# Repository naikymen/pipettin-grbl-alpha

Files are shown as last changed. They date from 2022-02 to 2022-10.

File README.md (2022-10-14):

# Development has moved to GitLab

New repoo at: https://gitlab.com/pipettin-bot/pipettin-grbl

# Pipettin' GRBL

Pipetting robotware for laboratory protocol automation.

> Proper documentation to build this yourself is not yet ready, let us know if you wish to get help, or help out :)

This repository contains hardware design files and software for a test prototype. 
Hardware is licenced under the [CERN-OHL-S](https://github.com/naikymen/pipettin-grbl-alpha/blob/master/HARDWARE_LICENCE.txt) licence 
and software under the [GNU GPLv3 licence](https://github.com/naikymen/pipettin-grbl-alpha/blob/master/SOFTWARE_LICENCE.txt) licence.

mender1_cdnm_mazinger

> Pardon our _castellano_ :)

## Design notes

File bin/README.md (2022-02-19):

# mongodb 3.2.12 binaries

Mongo compiled for 32-bit Raspbian in the Raspberry Pi 4. Unfortunately, the apt version did not work out for us.

See notes at `gui/README.md`.

## Startup commands

    sudo mongod --storageEngine=mmapv1

### Repair unclean shutdown

    sudo mongod --storageEngine=mmapv1 --repair
    sudo mongod --storageEngine=mmapv1

## CLI shell

    mongod

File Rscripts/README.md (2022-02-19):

# R code for pipettin-grbl

The PCR Mix protocol planner uses a custom R script, which clusters tubes by similarity into a dendrogram.
The resulting tree is cut, and intermediate solutions are prepared, reducing the amount of required pipetting steps,
and a consequently faster protocol. 

We use this version of R:

```
> R.version
               _
platform       arm-unknown-linux-gnueabihf
arch           arm
os             linux-gnueabihf
system         arm, linux-gnueabihf
status
major          3
minor          5.2
year           2018
month          12
day            20
svn rev        75870
language       R
version.string R version 3.5.2 (2018-12-20)
nickname       Eggshell Igloo
```

> R 3.5 is quite old, but this is what is packaged in `r-base` by our Ubuntu distribution for the raspberry pi.

## PCRmix protocol planner

### Requirements

* R 3.5.2
* Some packages: `install.packages(c("dendextend", "tidyr", "dplyr", "jsonlite"))`

### Code and usage

```sh
# First argument is the input JSON, and the second is the output JSON path
Rscript --vanilla ~/pipettin-grbl/Rscripts/pcr_planner.R ~/pipettin-grbl/Rscripts/sample_input.json ~/pipettin-grbl/Rscripts/sample_output2.json
```

See `pcr_planner.R`.

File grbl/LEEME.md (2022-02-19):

# Pipetting GRBL firmware

Vanilla GRBL 1.1h should work fine unless you need to control a servo (which you do need to use the tip ejector).

## Usage

Import this directory as a library in the Arduino IDE. Use the "grbl upload" example to burn GRBL onto the Arduino UNO.

If you have already installed the 10uF capacitor across the reset/abort pins (to prevent reset on serial reconnect), you may need to remove it temporarily before uploading the frimware (or you may get some errors while doing so).

## Testing

You may interact with GRBL from a linux terminal using `minicom`. For example:

```bash
minicom -D /dev/ttyACM0 -b 115200
```

Try typing `?` to check GRBL's status, or `$$` and pressing enter to see its settings.

The python scripts offer a rudimentary interactive text-based interface, using the `--interactive` option. That one wraps the serial interface, and controls other parts of the machine (i.e. the tool/pipette axis).

## Modifications

All major modifications are on the hardware side, specially on the Arduino CNC Shield 3.0 clone.

*IMPORTANT*: `ENABLE_DUAL_AXIS` and `VARIABLE_SPINDLE` are incompatible in our setup (though in theory its not impossible to enable them simultaneously).

### Servo control via Variable Spnidle PWM

If using a servo motor on the spindle enable pin, enable variable spindle with `#define VARIABLE_SPINDLE` (at line 339 of `config.h`).

The spindle PWM frequency is altered in `cpu_map.h` to be compatible with a hobby servo. Using a 1024 prescaler in fast-mode PWM we get `~60 Hz` which worsk great for ejecting tips.

Note: we tried to use this for the pipette axis. But the servo was not precise enough, and had a "bounce" effect which cannot happen during pipetting.

Ver wiki:

  * https://wiki.frubox.org/proyectos/diy/cnc#controlar-un-servo-con-el-spindle

### Dual Y axis Gantry squaring

This is disabled in our build. Our A axis clones the Y axis.

If you have dual X or Y axis (ie, two independent steppers and threaded rods for one direction of movement) enable gantry squaring with `ENABLE_DUAL_AXIS`. Follow the official GBRL documentation for correct configuration and limit switch setup.

## Configuration notes

I advise not using `$1=255` as it does not seem to play nice with our testing hardware (with A4988 drivers).

The full configuration for our setup makes GRBL work in positive space coordinates with origin at X0 Y0 by setting the masks correctly and issuing the corresponding G92 command after homing.

We also needed to reverse the Y axis and the XT homing direction. This is because the web-based GUI uses that coordinate system (right and down are positive the directions) and because reversing the homing direction will leave the machine at this origin (it otherwise homes to max X/Y instead of min X/Y).

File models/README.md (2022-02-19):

TODO: reorganizar este readme.

TODO: agregar info de modelos pasados a FreeCAD bajo `modelos_ejez_Z_y_S/basic_parts_freecad/`.

# Sujetador Jeringas y Pipetas

Sujetador Jeringa CNC Stepper.stl en modelos_ejez_Z_y_S/

Diseño en TinkerCAD para el "eje pipeteador" que usa:

  * Una jeringa
  * Stepper NEMA 17
  * Varillas de 8 mm
  * Varilla roscada de 8 mm con tuerca.
  * Tuercas y tornillos M3 / varilla roscada y tuercas de 3 mm

Link: https://www.tinkercad.com/things/gWPShCd3e0L-sizzling-lappi-borwo/edit

## Requires

  * `topeJeringa1mL` en modelos_pipetas_jeringas/

# topeJeringa1mL

Diseño en FreeCAD para la "T" en la parte de arriba del émbolo de una jeringa de 1 mL.

Marca "Bremen", marcada como: "Tuberculina 1mL con aguja 0.5 x 15 mm 25Gx5/8".

# Otro modelo

https://www.thingiverse.com/thing:1684481

https://www.tinkercad.com/things/aL2rLg0KME9

# Meshroom folders

Photogrammetry test, to digitize pipettes.

https://www.youtube.com/watch?v=1D0EhSi-vvc

https://meshroom-manual.readthedocs.io/en/latest/tutorials/sketchfab/sketchfab.html

# Notas

## Pipette tip dimensions

https://www.fts.co.nz/image/data/PDF/Pipette%20Tips.pdf

  * p1000 ~ 70 mm
  * p200 ~ 50 mm
  * p20 ~ 37-46 mm

Por lo tanto el eje Z debería poder viajar al menos 70 mm.

El eje Z del CNC solamente tiene 30 mm de viaje aproximadamente.

En un caso razonable, en el que haya un falcon de 50 en el workspace para usar con una p1000, el recorrido mínimo para poder pipetear todo debería ser 140 mm.

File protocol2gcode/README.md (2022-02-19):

# protocol2gcode

This python3 module works as three things:

* Interpreter: loads "protocol" actions and "platform" and "workspace" objects from MongoDB, defined previously through the GUI.
* Slicer: parses "actions" and generates "GCODE" for the protocol.
* Driver: controls GRBL, the pipette motor and the tip-eject servo motor. Sends commands to the machine (either from a predefined task/protocol in the mongo database or from a basic "interactive" interpreter).

## Commands: GCODE and Pseudogcode

### GCODE

"Vanilla" GCODE passed on to GRBL to move the XYZ axis.

The spindle `M3` command is used to eject tips (see electronics readme):

  * Eject: `M3 S20`
  * Retract: `M3 S150`

### Pseudogcode

Defined at `driverGcodeSender2.py`.

Used by the intepreter to move the pipette "P" axis:

  * `Phome;2` home the pipette and retract 2 mm away from the limit switch.
  * `Pmove;5` displace the pipette 5 mm
  * `Pmove;-5` displace the pipette -5 mm

It also supports a "wait" command:

  * `Wait;2` waits 2 seconds before parsing next line in the protocol.

The prefixes used (stuff beforethe semicolon) can be overriden.

## Dependencies

`sudo apt install python3-pip`

`pip3 install pyserial pigpio rpi.gpio`

`pip3 install pymongo==3.4.0`

La versión 3.10 no se lleva bien con mongodb disponible en los repositorios de Raspbian.

`sudo apt install pigpio`

`pip3 install python-socketio`

Note: installing bare 'socketio' may not work (https://github.com/miguelgrinberg/python-socketio/issues/264#issuecomment-518011401).

Note: if you find errors using "pip" to install the package in arch, try `sudo pacman -S python-socketio`

### pigpio and 64-bit OSes

There are some kernel problems. They were suposedly fixed in V71 or even before that, but i couldnt get it to work in Ubuntu Server 20.04 for RPi 4. The proposed solution involved:

  sudo nano /boot/firmware/cmdline.txt

Adding at the end of the line: `iomem=relaxed strict-devmem=0`

See: https://github.com/joan2937/pigpio/issues/259

## Usage

### Dry run

Useful for debugging.

```bash
sudo pigpiod
python3 main.py --protocol "Simple Protocol" --dry
```

### Stream full protocol interactively

Useful for debugging.

```bash
sudo pigpiod
python3 main.py --protocol "Simple Protocol" --interactive
```

### Stream full protocol

```bash
sudo pigpiod
python3 main.py --protocol "Simple Protocol"
```

## Testing

### Using minicom to interface with GRBL directly

minicom can be used as a "serial monitor" from the linux CLI:

```bash
minicom -D /dev/ttyACM0 -b 115200
```

Notes:

* Your keystorkes will not be echoed.
* To exit minicom, press "Ctrl+A" and then "Z".
* The Arduino may be unresponsive in some cases (for example, after asking for a reset; i.e. `[MSG: Reset to continue]`).

### GRBL-only testing

On a PC, the `GPIO` and `pipgio` libraries may not be available.

In which case, "mock" objects are imported from `dummyGPIO.py`.

This allows the code to send `GCODE` requiring only:

* An arduino with GRBL on it.
* Editing `python test_norpi.py` to your testing needs.

### Headless testing pre-requisites

To test this without the GUI, you must setup and populate the database with valid workspaces, protocols and platforms.

Briefly:

Install and start `mongod` on your computer.

Import the JSON files with' `mongoimport`, as specified by the `defaults/README.md` file.

# TO-DO

## Jogging

See:

  * https://github.com/vlachoudis/bCNC/blob/master/bCNC/controllers/GRBL1.py
  * https://github.com/gnea/grbl/wiki/Grbl-v1.1-Jogging

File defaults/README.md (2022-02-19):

# MongoDB default documents

- Platforms
- Workspaces
- Protocols

## export

    mongoexport -d <database> -c <collection_name> -o <output_file.json> --jsonArray

Examples:

    mongoexport -d pipettin -c platforms -o platforms_export.json --jsonArray

## import

In the Raspberry Pi 4 I had to append `--jsonArray` to these commands to fix the  following error: `BSON representation of supplied JSON is too large`

In my PC this was unnecesary, it's probably due to the old mongodb version on raspbian.

```bash
mongoimport --db pipettin --collection platforms --file platforms.json --jsonArray
mongoimport --db pipettin --collection platforms --file platforms_enanas.json --jsonArray
mongoimport --db pipettin --collection workspaces --file workspaces.json --jsonArray
mongoimport --db pipettin --collection protocols --file protocols.json --jsonArray
mongoimport --db pipettin --collection protocols --file protocols_for_tests.json --jsonArray
mongoimport --db pipettin --collection protocols --file protocol_test1.json --jsonArray
```

Can check with:

```
$ mongo
> use pipettin
> db.workspaces.find().pretty()
> db.protocols.find().pretty()
```

## update

Drop tables from mongo and reimport them using the commands above.

```
$ mongo
> use pipettin
> db.platforms.drop()
> db.protocols.drop()
> db.workspaces.drop()
$ git pull
$ mongoimport --db pipettin --collection platforms --file defaults/platforms.json
```

## troubleshooting

You may need to set "export LC_ALL=C" in bash if you get the following error:

    BadValue Invalid or no user locale set. Please ensure LANG and/or LC_* environment variables are set correctly

See: https://stackoverflow.com/questions/26337557/badvalue-invalid-or-no-user-locale-set-please-ensure-lang-and-or-lc-environme

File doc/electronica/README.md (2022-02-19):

# Electronics

El diagrama de conexiones está en el archivo `diagrama_conexiones`.

El formato `cddx` puede editarse en: https://www.circuit-diagram.org/editor/

## RPi as master controller

### Connections

To GRBL, using a standard USB cable.

To the Pololu and the limit switch, using the GPIO header.

To the arduino reset pin, from the GPIO header and through a transistor.

### Pipette pololu capacitor

Prevents voltage spikes :) it is connected across the main 24 Volt line.

## CNC Shield 3.0 and Modifications

A CNC Shield v3.0 clone.

### Pololu Vref adjustment

Set to 1.1 V, limiting total machine current to less than 2 A. Could be less I guess, haven't tested.

https://wiki.frubox.org/proyectos/diy/cnc#ajuste-vref-pololu

More voltage means more reliable stepping, and means less current, which means less heat.

### Cooling fan

Stepper drivers can overheat at higher Vref without a cooling fan.

In all cases, the longer the run the more important cooling became.

Use a fan always, just in case.

### Clone the Y axis to A

We have a double Y axis, pins are setup accordingly.

Note: no square gantry, its incompatible with our 3.0 shield clone.

### Invert pins 11 and 12

Tu use with variable spindle GRBL 1.1h, we inverted pins 11 and 12.

This allows us to use the variable spindle PWM function to drive a servo (see `grbl/LEEME.md`).

See also: https://wiki.frubox.org/proyectos/diy/cnc#z-axis-limit-switch

### Servo-motor for tip ejection

Using the default pin for variable spindle in GRBL 1.1h (note that a rewire is important if using an old CNC Shield v3.0 clone; this is described above).

5V step-down power supply.

### Reset pin capacitor

Putting a capacitor between reset and GND prevents arduino reset on pyserial open/reconection (it also prevents uploading new firmware, do it after flashing GRBL :).

https://forum.arduino.cc/index.php?topic=21479.msg159720#msg159720

### Arduino reset from GPIO

Sometimes the Arduino needs to be reset by the RPi.

The voltages are different (3.3V GPIO vs 5V Arduino).

So, a transistor is useful for resetting/unlocking GRBL.

We used a PNP transistor in stead of an NPN, but the concept is the same as in: https://electronics.stackexchange.com/a/180709

### Stepper wiring and directions

Important for correct workspace coordinate system.

See: https://wiki.frubox.org/proyectos/diy/cnc#stepper-wiring-y-sistema-de-coordenadas

### End-stops and modifications

Important for homing.

## CNC shield hat

A small hat to tidy up some of the modifications of the CNC Shield described previously.

KiCAD designs for the hat are in the `cnc_shield_hat` directory.

Also, KiCAD designs for the a CNC Shield are in the `sb-cnc-shield` (cloned repository from GitHub, not used here).

Settings for pcb2gcode[GUI] and a sample command are in the `pcb2gcode` directory.

### KiCAD 101

A simple video showing the basic workflow: https://www.youtube.com/watch?v=-tN14xlWWmA

### Installing and using pcb2gcode

This translates gerber files to millable gcode.

pcb2gcode might be moderately hard to install. I had to modeify a header file on `gerbv` 's source code for it to compile on modern GCC.

Then, to compile `pcb2gcode` with the headers in the `gerbv` I built in the previous step, it is important to set an environmen variable before running `./configure`:

    export PKG_CONFIG_PATH=~/Software/pcb2gcode/gerbv-2.7.0/src

The GUI was cloned, built, and installed without issues on my system.

There are some GRBL-specific configurations for `pcb2gcode`. Once taken into account, only minor modifications of the gcode are necessary.

Read for details: https://wiki.frubox.org/proyectos/diy/cnc/kicad_pcb

### Preview of the GCODE

This can be done on bCNC directly or on http://chilipeppr.com/grbl (or http://chilipeppr.com/jpadie).

### Editing and sending gcode with bCNC

The only important edits are:

  * Optional: add a homing cycle and your G92 command.
  * Remove unnecessary header commands.

https://wiki.frubox.org/proyectos/diy/cnc#bcnc

# To-do 

Completar este readme.

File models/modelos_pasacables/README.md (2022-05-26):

# Concept

* https://en.wikipedia.org/wiki/Cable_carrier

# FreeCAD models

These are the final models (see `freecad_port_models/`).

Port of [Gasolin's work](https://www.thingiverse.com/thing:4375470).



# Thingiverse models

* Esta tiene infinitos likes, parece que es la que va: https://www.thingiverse.com/thing:1078216
* https://www.thingiverse.com/thing:2125076
* https://www.thingiverse.com/thing:204791
* Pero me gustó más esta: https://www.thingiverse.com/thing:4375470

## Chosen model

Thing 4375470 (chain_link_v2-Clip.scad) at https://www.thingiverse.com/thing:4375470

## Model issues

We tried tolerances 0.1, 0.2 and 0.3. Unfortunately all presented problems:

  * 0.1 was too small, and movement was impaired.
  * 0.2 and 0.3 were too loose, allowing bending of the chain in the wrong direction.

### Chain clip problem

The original clips fit too tight.

Placing the clip deforms the model a little so that the hinges move more freely.  A slowly deforming clip will eventually fail, and the hinges may become lodged again. So putting less stress on that part (i.e. by making it wider or ncreasing tolerance) seems prudent.

## Solution

Since no compromise in "tolerance" was good enough, we modified the OpenSCAD model to fit our needs:

  * Setting `under_angle=-4;` will fix the tolerance problem (line 29) producing chains that do not bend in the opposite direction.
  * Added a `clip_extra_width = 0.5;` and `clip_extra_tolerance=0.05` parameters to relax the clip a little (line 44 and 45).
  * several other patches are mentioned below...

### Patches and explanation

Setting `under_angle=-4;` in the original version of the model caused some weird artifacts to appear. We removed them by subtracting two cubes in the seemingly "right" places (lines 98 and 126).

Also, this setting made the base of the chain detach from the baseplane in the original model. While this might have been intentional, it has two problems:

  * Makes printing harder.
  * Causes the links to lock less tightly, in a way that the "under angle" is less than expected (i.e. when setting `under_angle=-4;` you actually get less).

To fix this I added two blocks of the right height at the base of each side of the chain module (line 66 and 67). 

----

Added a 0.005 offset and enlarged one of the cubes in the `outline` module, which removed a strange visual artifact (line 73).

----

The clip tolerance was applied to the slot, but not to the clip. While this may have been intentional now there is a `clip_extra_tolerance=0.05` setting for that (line 45; the default used to be 0).

----

There was a small notch in the material that appears when setting `under_angle=-4;`. This is due to rotation of the cube at line 172. I moved the rotation function so that it only affects the `middle_0` module, and not the cube at line 172.

## Printing notes

An accurate first layer is important in this model to prevent bending of the chain in the wrong direction.

Squashed frist layer or elephants foot must be avoided. If the first layers print wider than expected, the hinges will become stuck on assembly. On the other hand, if they are smaller the chain will bend in the wrong direction more easily.

Proper calibration of the first layer height and/or using elephant's foot compensation may be important.

## Post-printing

Adding some graphite dust can help with lubrication and extend durability of the hinges.

# Changelog

## v0.1

Working cable carrier model.

## v0.2

Incremente el "underangle" un poco. Las orugas más largas se doblan un poco hacia adentro todavía :/

Pasó de -4 a -4.5 en el archivo openscad.

## v1.0

Port del modelo a FreeCAD, con mounting holes.

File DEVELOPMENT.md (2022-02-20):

3) Guia de contributing/developer (todo lo que hay hoy en los readme basicamente)
 - Explicacion de la arquitectura
 - Explicacion de cada modulo (protocol2gcode, gui, etc) y como usarlos y correrlos por separado
 - Como instalar los requires (mongo, python, etc) desde 0 en una raspberry pelada u otro linux

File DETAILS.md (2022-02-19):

# Pipettin' GRBL

Pipetting robotware for laboratory protocol automation.

mender1_cdnm_mazinger

## Installation on RPi 4

Restore our SD card image:

```
gunzip --stdout pipettin_pi.img.gz | sudo dd bs=4M of=/dev/YOUR_SD_CARD_DEVICE
```

See: https://www.raspberrypi.org/documentation/linux/filesystem/backup.md

Background services are managed by `systemd` user units `commander.service` and `nodegui.service` (both defined at `/home/pi/.config/systemd/user`, enabled by default).

## Requirements

Requirements _at a glance_.

### Hardware

* Raspberry Pi 4 (a Pi 2 would probably do too).
* Arduino Uno.
* Arduino CNC Shield (v3.0.0 will do, improved functionality of GRBL is enabled with later versions), stepper drivers, and two capacitors in the 100 uF range.
* A "Gilson-style" p200 micropipette.
* Any CNC or 3D printer hardware (i.e. frames, guides, threaded rods or pulleys, steppers, limit switches, 3d printed parts, bearings, etc. TODO: make a BOM).
* Power supply (at least 12 V, steppers are best driven at just below the maximum voltage rating of the driver, AFAIK).
* Laboratory consumables: p200 pipette tips, tube racks, tubes, reagents, etc.

### Software

Raspberry Pi requires: Node, MongoDB, python3, and R (optional, for PCRmix protocol builder). We suggest using our custom system image.

Arduino requires: GRBL v1.1h

Your client computer requires: a modern browser.

### Other requirements

A WiFi network, where the Pi and the client can reach each other.

## Software architecture

1. The GUI generates "workspaces" by using platforms as "templates" and filling the `content` of them regarding user definitions in the UI.
2. Then the user defines a "protocol" for that workspace (a sequence of operations over objects in the workspace). The GUI translates the protocol into "High Level Commands" as representations of each operation or group of operations.
3. The "protocol2gcode" python3 module interprets these commands sequentially, and streams the necessary GCODE to the hardware firmware (modified GRBL 1.1h).

Templates for the definitions (of workspaces, protocols, and platforms) are in JSON format. Those must be imported to your local mongodb server (learn more at the [protocol2gcode](#protocol2gcode) section).

## Software modules

### GUI

Express.js webapp to create workspaces, contents and protocols.

### protocol-builder

JS library that interprets the user input, and generates protocol.json files.

### workspace-builder

JS library that interprets the user input, and generates workspace.json files.

### protocol2gcode

Python library that interprets protocol files and generate/stream GCODE to grbl.

After the GUI defines workspace, platforms and protocol, it saves all elements it in the mongodb database.
Then, it calls this python library to interpret it, and generate/stream the GCODE to grbl.

The library runs as a systemd service, and communicates with the GUI through SocketIO.
It can be used without the GUI, as long as the workspace objects are in the Mongo database.

See [protocol2gcode/README.md](protocol2gcode/README.md) and [defaults/README.md](defaults/README.md) for instructions on setting up testing without the GUI, using the default JSON templates.

## Arduino Firmware

GRBL was configured in "gantry" mode: two independent steppers and end stops for the Y axis.

## Hardware

Hardware _at a glance_.

### Electronics

* Arduino UNO with CNC Shield 3.0 (clone) and limit switches.
* Raspberry Pi 4.
* Pololu stepper drivers.
* Two buck converters, a capacitor and a transistor.
* Power supply.

Se details at the dedicated [documentation](doc/electronica/README.md) page.

### Structure and Mechanics

Our designs for parts are still being tested, find them in the "models" directory. See the README.md files therein.

Since the micropipette does not need as much structural stiffness in the XYZ axes as a spindle CNC machine, any CNC or 3D printer structure would work just fine.
However, it should withstand the force needed to place a pipette tip.

I other words, you are not bound to use our models, except for the pipette tool adapter (also refered to as the "S axis" elsewhere), attached to the CNC's head.

# In action

We will eventually post some eye candy here.

here comes the airplane!

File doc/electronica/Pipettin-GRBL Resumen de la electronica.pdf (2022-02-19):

## Resumen

El aparato es básicamente un CNC cartesiano.

Los componentes principales son:
- 1x Arduino Uno + CNC shield 3.0
- 1x Raspberry Pi 4 (modelo B).

Otros componentes:
- Fuente de 24 V
- Ventilador 12 V (+ fuente step-down)
- Pololu DRV8825

### Arduino

Firmware: GRBL 1.1h
Controla:
4x DRV8825 para 3 ejes cartesianos (doble motor para el eje Y). Lee:
4x sensores mecánicos de fin de carrera.

### Raspberry

SO: Raspbian
Controla:
| 1x Arduino Uno (por USB + reset pin) 1x DRV8825 (por GPIO) para el cuarto eje. [otros módulos]

Lee:
| 1x End-stop switch

## Pedido

Necesitamos una forma de organizar todos estos componentes. Idealmente uno o varios circuitos en PCB, que se puedan conectar fácilmente al Raspberry o CNC-shield.
Lo más parsimonioso parece ser hacer: (1) un PCB independiente para la alimentación, (2) un “hat” para el CNC-shield, y (3) otro “hat” para el Raspberry Pi.

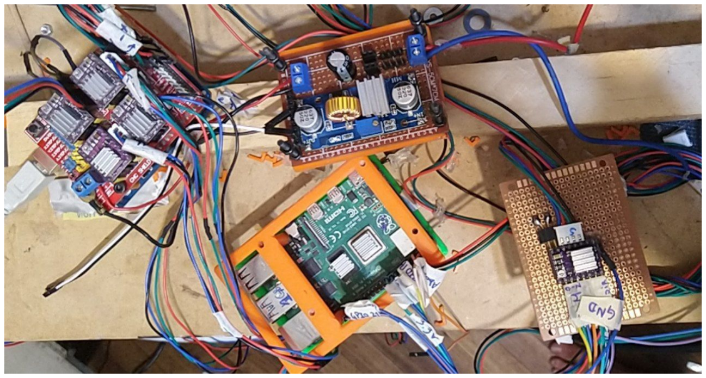
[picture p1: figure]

El “hat” para el CNC-shield ayudaría a organizar los cables de los end-stops, pero no es prioritario.

### Diagrama del circuito

El RPi controla el DRV8825 (con PWM por pigpio). DRV8825 es alimentado por una fuente de 24V (DC) con un capacitor en paralelo. Una fuente step-down alimenta un ventilador para refrigerar los DRV8825. El RPi puede resetear el Arduino por medio de un transistor (que pasa la señal de 3.3V del GPIO al reset pin del Arduino, que funciona con 5V).

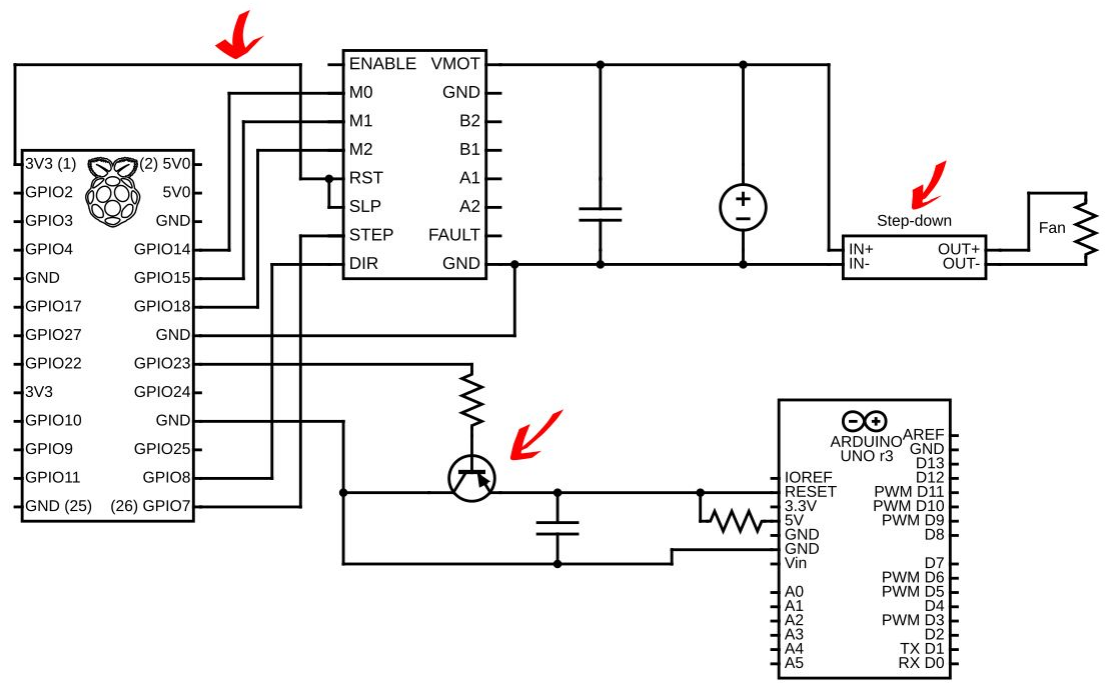
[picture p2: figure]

## Wiki

https://wiki.frubox.org/proyectos/labware/pipettin-grbl

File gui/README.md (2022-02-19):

# GUI

## Structure

En backend de NodeJS.

Todo empieza en "bin/www", que levanta un servidor http de Node y sirve lo que está en "public/".

Para cada ruta o path del URL hay un handler en app.js.

La ruta principal "/" va a "routes/index.js" que de acuerdo al URL renderea algun template de la carpeta "views/".

Tamibén está lo que devuelve JSON en "rotes/mainApi.js"

Las funciones del HTML estan todas en "public/js/app.js".
Por ejemplo "saveNewPlatform()" hace un "POST" request a la API de platforms para guardar el JSON de una platform en mongo.

Observaciones:

* las rutas de un router ("routes/") son relativas a como se declararon en el "app.js" (usando el comando "app.use()").
* en los request handlers, "res.json" es equivalente a un "return()" de un objeto json en otros lenguajes. Podria ser "res.send" para mandar texto plano, etc.
* Las formas de los contents son dibujadas por "public/js/app.js drawContent()". El orden de los elementos del SVG (en "z") corresponde con el orden del agregado de elementos en "drawContent()".
* Los colorcitos de los tags se arman por hash en "views/workspacePanel.ejs".
* No se puede compartir el código del frontend (en "public") y del backend (en "views" y "routes") al mismo tiempo.
* El joystick está en "public/js/joystick.js".
* Hay un "public/css/style.css". El "#" es un "id" de un HTML tag, y el "." corresponde a una "clase" de un HTML tag.

## Requirements

- node.js
- mongodb > 2.6

```bash
sudo apt install nodejs npm pkg-config libusb-1.0-0-dev libudev-dev
sudo systemctl enable mongodb
```

### Building and installing mongodb 3.2.12 on Raspbian 32-bit

Mongo needs to be > 2.6 to work with the node driver. see: https://mongobooster.useresponse.com/topic/wire-version

I followed this guide: https://koenaerts.ca/compile-and-install-mongodb-on-raspberry-pi/

#### Prepare

```bash
sudo apt update
sudo apt upgrade
sudo apt install wget scons build-essential
sudo apt install libboost-filesystem-dev libboost-program-options-dev libboost-system-dev libboost-thread-dev
sudo apt install python-pymongo

mkdir -p mongo/install
cd mongo/install
wget https://fastdl.mongodb.org/src/mongodb-src-r3.2.12.tar.gz
# https://github.com/mongodb/mongo/archive/r3.2.12.tar.gz
tar xvf mongodb-src-r3.2.12.tar.gz
cd mongodb-src-r3.2.12

sudo dd if=/dev/zero of=/mytempswapfile bs=1024 count=524288
sudo chmod 0600 /mytempswapfile
sudo mkswap /mytempswapfile
sudo swapon /mytempswapfile
```

Prepare some more:

```bash
cd src/third_party/mozjs-38/
./get_sources.sh
./gen-config.sh arm linux
cd -
```

#### Build

First edit some files:

- Add `#include sys/sysmacros.h` to the file `src/mongo/db/storage/mmap_v1/mmap_v1_engine.cpp`

> There are some warnings treated as errors by cc1plus, so disable that behaviour and compile anyway. I skipped compilation of mongos.

Then build:

```bash
scons mongo mongod --wiredtiger=off --mmapv1=on --disable-warnings-as-errors  # guessing i do not need mongos
```

Reduce binary sizes:

```bash
strip -s mongo
strip -s mongod
```

#### Compilation notes

At first i tried to compile by ignoring two warnings by adding lines to the SConstruct file after `if myenv.ToolchainIs('clang', 'gcc')`:

```
        # AddToCCFLAGSIfSupported(myenv, '-Wno-parentheses')
        # AddToCCFLAGSIfSupported(myenv, '-Wnonnull-compare')
```

But the `nonnull-compare` warning was still raised as an error. I do not know what I am doing... so please help improve this if you know how :)

I did not look at all warnings during compilation so there may be other type of ignored warnings. Like "-Wstringop-truncation" (?)

#### Install and cleanup

Install:

```bash
cd build/opt/mongo
sudo cp mongo mongod /usr/local/bin/
```

Cleanup:

```bash
reboot
sudo swapoff /mytempswapfile
sudo rm /mytempswapfile
```

#### Configure mongod

Edit `/etc/mongod.conf` such that:

```
# mongod.conf

# for documentation of all options, see:
#   http://docs.mongodb.org/manual/reference/configuration-options/

# Where and how to store data.
storage:
  dbPath: /var/lib/mongodb
  journal:
    enabled: true
  engine: mmapv1
#  mmapv1:
#  wiredTiger:

# where to write logging data.
systemLog:
  destination: file
  logAppend: true
  path: /var/log/mongodb/mongod.log

# network interfaces
net:
  port: 27017
  bindIp: 127.0.0.1
```

The most important bit is the `engine: mmapv1` setting.

#### Enable run on boot

Using `/etc/rc.local`, adding the following line before `exit 0`:

```bash
mongod --config /etc/mongod.conf
```

**NOT USED**. Enable unit service:

```bash
sudo systemctl enable mongodb
```

**NOT USED**. Using init:

* `/etc/init.d/mongodb`
* Which uses the config file: `/etc/mongodb.conf`

### Manually start mongod

```bash
sudo mongod --storageEngine=mmapv1
```

### Install mongotools

https://github.com/mongodb/mongo-tools

The defaults from raspberry pi repos worked for the `mongoimport` command.

See `defaults/README.md` for usage examples.

## Start the GUI

There is a systemctl service unit for this now. See files in the `systemd.units` directory.

Open the GUI by visiting http://localhost:3333

To start it manually, `cd` to the `gui` directory and run:

```bash
npm install  # is this necessary?
node bin/www
```

## TODO

- refactor frontend (app.js)
- error handling for protocol builder (now the step is skipped if there is a missing requirement)
- global config in mongo (area size, etc)
- import  steps
- item overwrite options (color, max volume, default heights)
- do not allow to refresh the page
- enhance content selection and multi tag
- allow background for petri and rotation option 
- allow "all" in targets/sources selection in protocol step

## Bugs

- Step selection is not working sometimes
- Save protocol is not saving if you are in a text area (programate click)

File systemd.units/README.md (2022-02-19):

# Systemd units for pipetting-grbl

Unit definitions reside at `~/.config/systemd/user/`.

After editing a unit, reload them with `systemctl --user daemon-reload`.

**Importantly**, run `sudo loginctl enable-linger $USER` at least once as the `pi` user.

Also run `sudo apt-get install python-systemd python3-systemd` to install the systemd modules required by the "commander" unit.

Some status info is printed on login by bash (see ~/.bashrc).
use standard systemctl commands to check on the services manually.
For example:

```bash
systemctl --user status nodegui.service
systemctl --user status commander.service
```

Useful bash aliases:

```bash
alias commander_restart='systemctl --user restart commander.service; journalctl --user-unit commander -f'
alias gui_restart='systemctl --user restart nodegui.service; journalctl --user-unit nodegui -f'
```

## Node "GUI" unit

Located at: `systemd.units/nodegui.service`

For development, this file uses `nodemon` instead of `node`. A compatible (legacy) nodemon version was installed with:

```bash
sudo npm install -g nodemon@2.0.12 # Details at https://github.com/remy/nodemon/issues/1948#issuecomment-953665876
```

The unit file should use `node` instead, for deployment.

## Python3 "commander" unit

Located at: `systemd.units/commander.service`

Learn more about it in `protocol2gcode/commander.py `.

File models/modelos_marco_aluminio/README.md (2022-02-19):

# v1.0

Funcionan, aunque no son fáciles de ensamblar.

# To-do

- [ ] Agregar tolerancias para facilitar el ensamblado.
- [ ] Diseñar patas y piezas para sostenerlas.
- [ ] Diseñar piezas para una "mesita" que sostenga la electrónica (o algo así).

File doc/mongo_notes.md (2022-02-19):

# Start on boot

Este no funcionaba porque estaba "masked":

https://askubuntu.com/questions/61503/how-to-start-mongodb-server-on-system-start

Se puede des-enmascarar, es una version mas fuerte de "disable":

https://askubuntu.com/questions/919108/error-unit-mongodb-service-is-masked-when-starting-mongodb

https://askubuntu.com/questions/710420/why-are-some-systemd-services-in-the-masked-state

## /etc/rc.local

No hay un "service" de systemctl para mongod.

Agregar esta linea a `/etc/rc.local`:

    mongod --config /etc/mongod.conf

Tal que `/etc/mongod.conf` contenga:

```
# mongod.conf

# for documentation of all options, see:
#   http://docs.mongodb.org/manual/reference/configuration-options/

# Where and how to store data.
storage:
  dbPath: /var/lib/mongodb
  journal:
    enabled: true
  engine: mmapv1
#  mmapv1:
#  wiredTiger:

# where to write logging data.
systemLog:
  destination: file
  logAppend: true
  path: /var/log/mongodb/mongod.log

# network interfaces
net:
  port: 27017
  bindIp: 127.0.0.1

######## Y SIGUE ... ######
```

Probar is anda corriendo `sudo mongod --config /etc/mongod.conf`

Si tira error de que falta `/var/log/mongodb/mongod.log`, crearlo con `sudo touch /var/log/mongodb/mongod.log`.

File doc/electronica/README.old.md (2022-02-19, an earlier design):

TO-DO:

* Como se conectaron los limit-switches (en particular para el doble eje Y).
* Como se concta el reset del Arduino al GPIO del Pi.
* Alimentación.
* Pololus, refrigeración y ajuste de Vref.
* Conexion GPIO a Pololu y limit-switch del eje S.

...

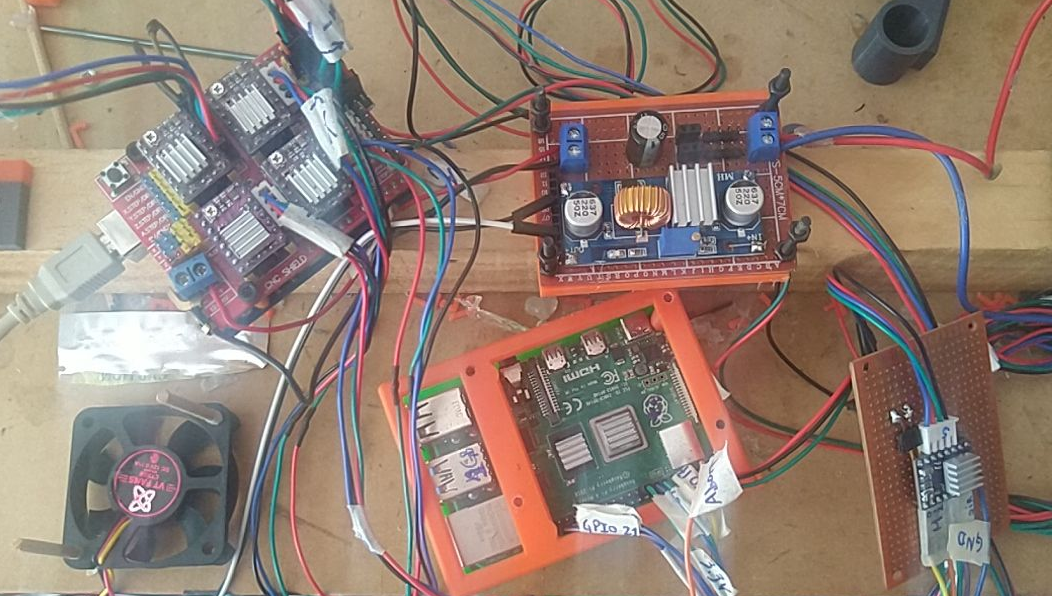
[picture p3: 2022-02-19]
doc/media/pics/20_12-barebones/robot_electronica_desarmada.png

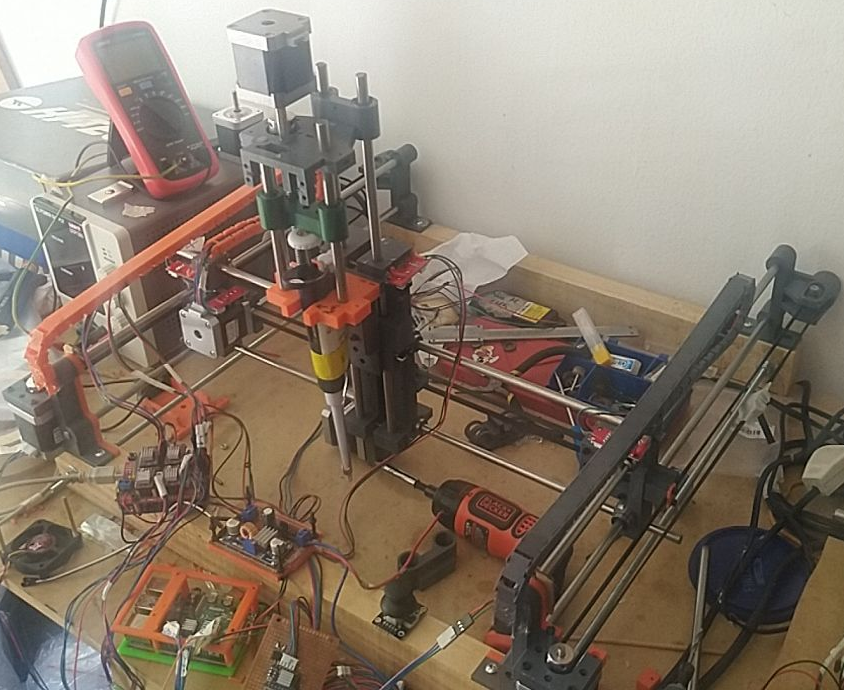
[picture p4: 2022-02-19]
doc/media/pics/20_12-barebones/robot_overview.png

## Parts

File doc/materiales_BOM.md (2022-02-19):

# Proveedores

* PrintALot
* https://mercadolibre.com.ar
* https://openhacks.com.ar

Spreadsheet:

* https://docs.google.com/spreadsheets/d/1nqJSYZ-nrdTaSJ7H5JYSDX2zimCQpnCKh9CfUzj1nbE/edit#gid=0

----

# Electro-Mecánica

## Estructuras

Partes impresas en PLA.

TO-DO.

## Motores

Paso a paso.

* 5 x NEMA 17 con paso de 1.8°

## Poleas

De 10 mm de ancho.

* 3 x poleas dentadas 10mm de ancho y 12mm de radio.
* 3 x poleas lisas para tensar.

## Varillas lisas

De 8 mm de diámetro, para los ejes XY.

## Varillas roscadas y tuercas

Para los ejes Z y S.

* 2 x varillas
* 2 x tuercas

## Rulemanes lineales

Para las varillas de 8 mm de diámetro.

* 8 x rulemanes lineales de 15 mm de diametro externo.

TO-DO: longitud

## Rulemanes comunes

Para soportar la rotacion de la varilla roscada del eje Z.

* Rulemanes Abec 7 608zz

## Ventiladores de refrigeración

Para refrigerar los stepper drivers.

* 1 x Ventilador de 5 V ???

TO-DO: modelo

TO-DO: quizás sea reemplazable por un disipador grande o dos largos, especialmente si consideramos hacer un PCB adaptador entre el arduino y el 3.0 clone.

----

# Módulos para manejo de líquido

### Micropipeta

* 1 x Micropipeta Gilson p200

### Tips y descartes

TO-DO

----

# Electrónica

## Controladores

* 1 x Raspberry Pi 4
* 1 x Arduino UNO

## CNC Shield y PCBs

TO-DO

* 1 x Arduino CNC shield clone (v3.0).
* ? x PCBs extra ???

## Sensores de fin de carrera

* 5 x ???

TO-DO: modelo.

TO-DO: Ojo con el problemita ese de la compatibilidad con el CNC shield.

## Stepper drivers

* 5 x DRV8825 (o A4998).

## Fuentes

* 1 x Fuente 24 V DC, de 3A.
* 1 x Fuente DC step down (para bajar a 5V).

## Otros

### Capacitores

### Resistores

### Transistores

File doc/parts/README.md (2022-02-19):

Carpeta con imágenes de los componentes que compramos.

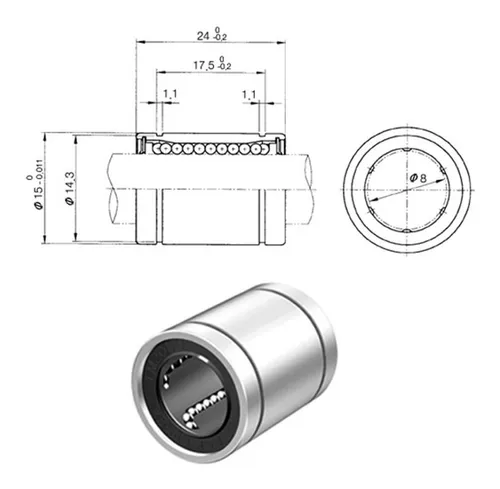
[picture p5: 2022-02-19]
doc/parts/Rodamientos Lineales Lm8uu.png

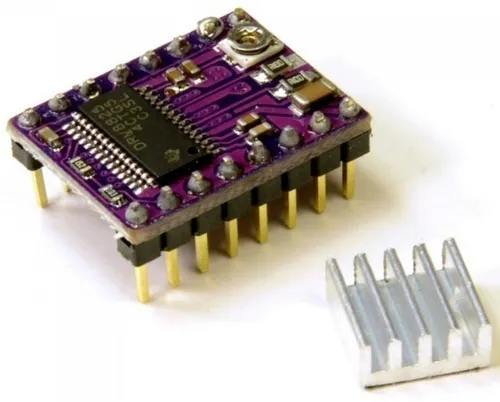
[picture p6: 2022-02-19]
doc/parts/pololu_drv8825_con_disipador.png

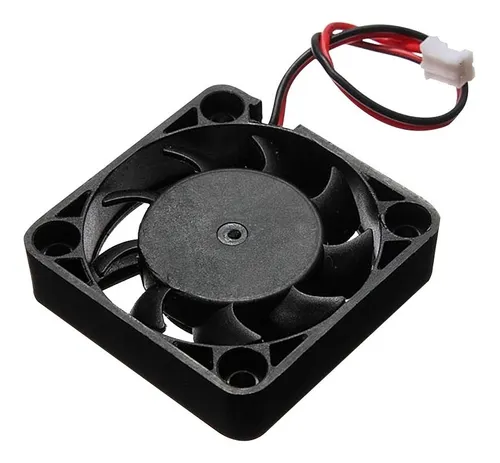
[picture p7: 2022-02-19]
doc/parts/ventilador_12V.png

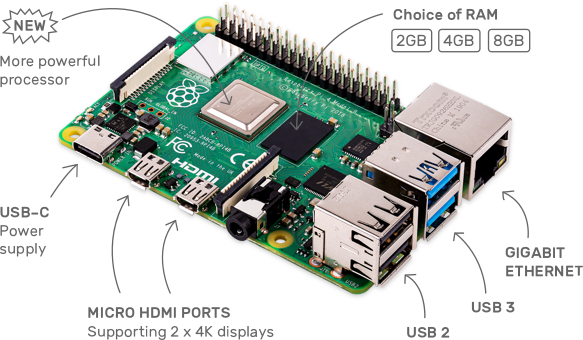
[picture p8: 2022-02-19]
doc/parts/raspberry-pi-4.png

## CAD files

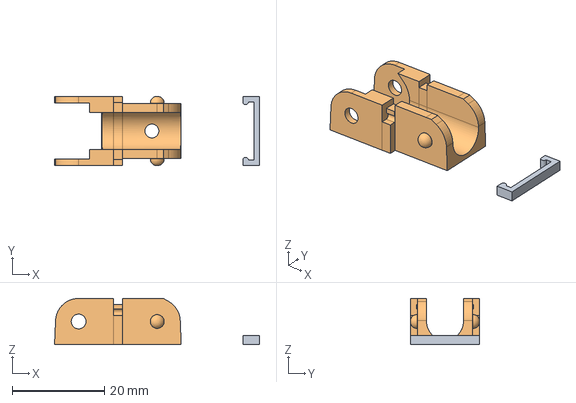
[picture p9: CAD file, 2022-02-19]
models/modelos_pasacables/freecad_port_models/cable_carrier-assembly.FCStd
44.4 x 15.0 x 10.0 mm
cable_carrier_separator_clip_001
cable_carrier_assembly

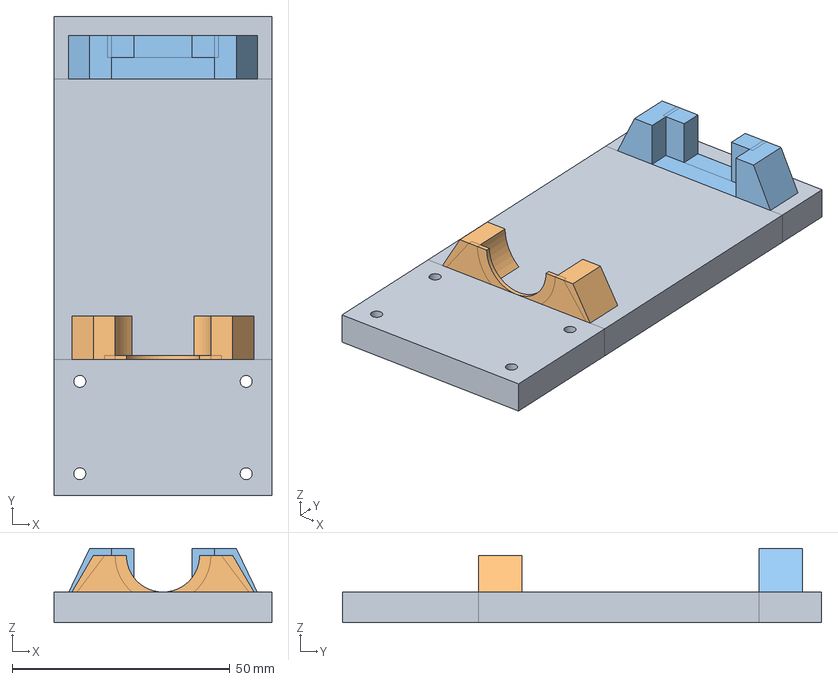
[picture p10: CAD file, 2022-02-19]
models/modelos_pipetas_jeringas/gilson_adapter_freecad/assembly.FCStd
50.0 x 110.0 x 17.0 mm
adaptador_gilson_001
adaptador_gilson_002
adaptador_gilson_003

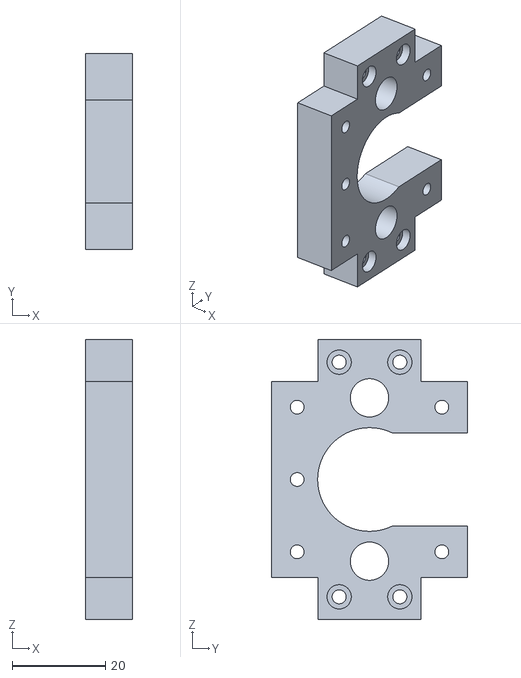
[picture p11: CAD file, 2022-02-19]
models/modelos_XYZS/freecad_base_models/base_stepper_Z-full_model.stl
10.0 x 42.0 x 60.0

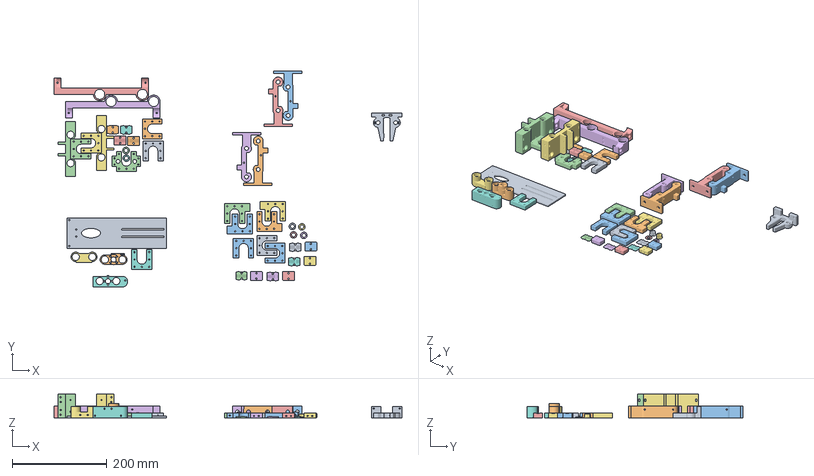
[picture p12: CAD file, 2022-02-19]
models/modelos_XYZS/Pippetin-grbl v0.9.3 - lm12uu X axis FULL.3mf
734.6 x 455.3 x 50.0 mm
Pippetin-grbl v0.9.3 - lm12uu X axis FULL.stl_1
Pippetin-grbl v0.9.3 - lm12uu X axis FULL.stl_2
Pippetin-grbl v0.9.3 - lm12uu X axis FULL.stl_3
Pippetin-grbl v0.9.3 - lm12uu X axis FULL.stl_4
Pippetin-grbl v0.9.3 - lm12uu X axis FULL.stl_5
Pippetin-grbl v0.9.3 - lm12uu X axis FULL.stl_6
Pippetin-grbl v0.9.3 - lm12uu X axis FULL.stl_8
Pippetin-grbl v0.9.3 - lm12uu X axis FULL.stl_10
Pippetin-grbl v0.9.3 - lm12uu X axis FULL.stl_11
Pippetin-grbl v0.9.3 - lm12uu X axis FULL.stl_12
Pippetin-grbl v0.9.3 - lm12uu X axis FULL.stl_13
Pippetin-grbl v0.9.3 - lm12uu X axis FULL.stl_14
Pippetin-grbl v0.9.3 - lm12uu X axis FULL.stl_15
Pippetin-grbl v0.9.3 - lm12uu X axis FULL.stl_16
Pippetin-grbl v0.9.3 - lm12uu X axis FULL.stl_17
Pippetin-grbl v0.9.3 - lm12uu X axis FULL.stl_18
Pippetin-grbl v0.9.3 - lm12uu X axis FULL.stl_19
Pippetin-grbl v0.9.3 - lm12uu X axis FULL.stl_22
Pippetin-grbl v0.9.3 - lm12uu X axis FULL.stl_23
Pippetin-grbl v0.9.3 - lm12uu X axis FULL.stl_24
Pippetin-grbl v0.9.3 - lm12uu X axis FULL.stl_25
Pippetin-grbl v0.9.3 - lm12uu X axis FULL.stl_26
Pippetin-grbl v0.9.3 - lm12uu X axis FULL.stl_29
Pippetin-grbl v0.9.3 - lm12uu X axis FULL.stl_30
Pippetin-grbl v0.9.3 - lm12uu X axis FULL.stl_31
Pippetin-grbl v0.9.3 - lm12uu X axis FULL.stl_32
Pippetin-grbl v0.9.3 - lm12uu X axis FULL.stl_34
Pippetin-grbl v0.9.3 - lm12uu X axis FULL.stl_35
Pippetin-grbl v0.9.3 - lm12uu X axis FULL.stl_36
Pippetin-grbl v0.9.3 - lm12uu X axis FULL.stl_37
Pippetin-grbl v0.9.3 - lm12uu X axis FULL.stl_38
Pippetin-grbl v0.9.3 - lm12uu X axis FULL.stl_39
Pippetin-grbl v0.9.3 - lm12uu X axis FULL.stl_40
Pippetin-grbl v0.9.3 - lm12uu X axis FULL.stl_41
Pippetin-grbl v0.9.3 - lm12uu X axis FULL.stl_42
Pippetin-grbl v0.9.3 - lm12uu X axis FULL.stl_43
Pippetin-grbl v0.9.3 - lm12uu X axis - reestablecer ancho carrito X.stl_1
Pippetin-grbl v0.9.3 - lm12uu X axis - reestablecer ancho carrito X.stl_2
Pippetin-grbl v0.9.5 - lm12uu X axis - second Z carriage.stl
Pippetin-grbl v0.9.5 - lm12uu X axis - Z carriage endstop screw.stl
Pippetin-grbl v0.9.5 - lm12uu X axis - Z base pad.stl
Pippetin-grbl v0.9.5 - lm12uu X axis - carrito S with end stop mount.stl

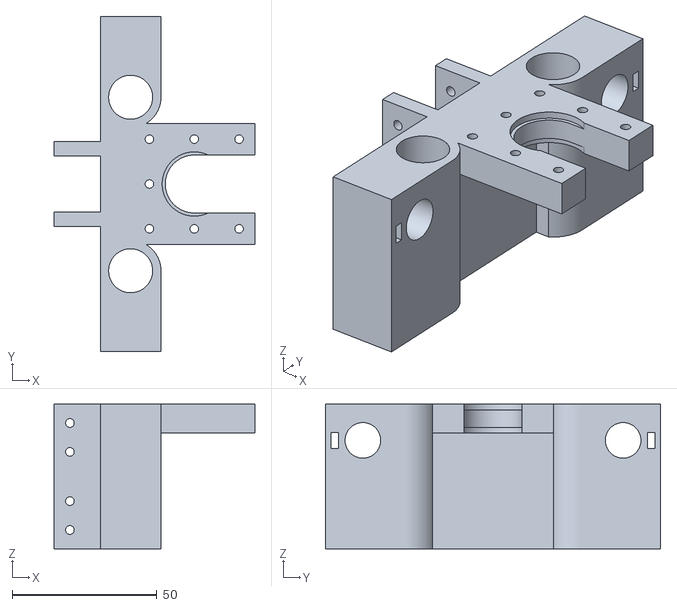
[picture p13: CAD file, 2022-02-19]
models/modelos_XYZS/freecad_base_models/base_X_lm12uu_slider_Y-full_model-assemblyA2plus.stl
69.5 x 116.0 x 50.0

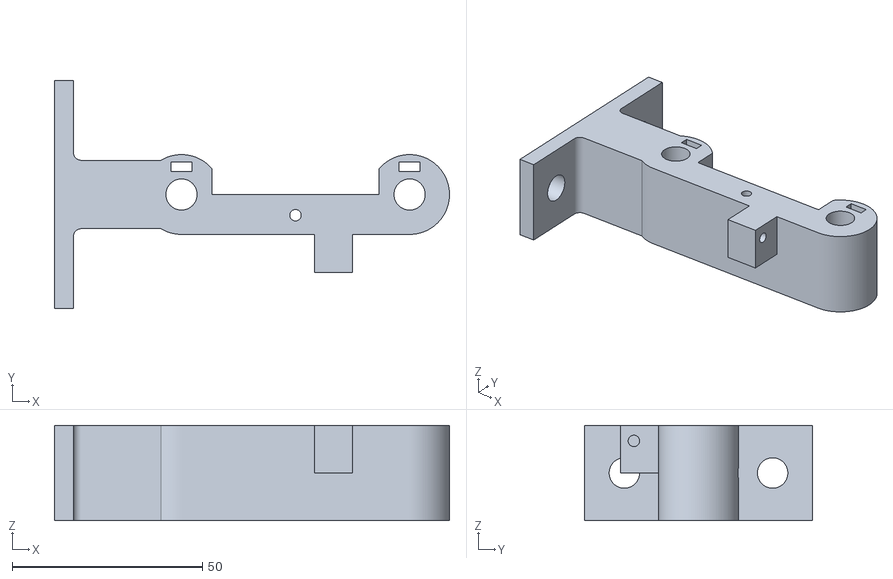
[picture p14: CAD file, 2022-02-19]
models/modelos_XYZS/freecad_base_models/base_varillas_Y-full_model.stl
103.9 x 60.0 x 25.0

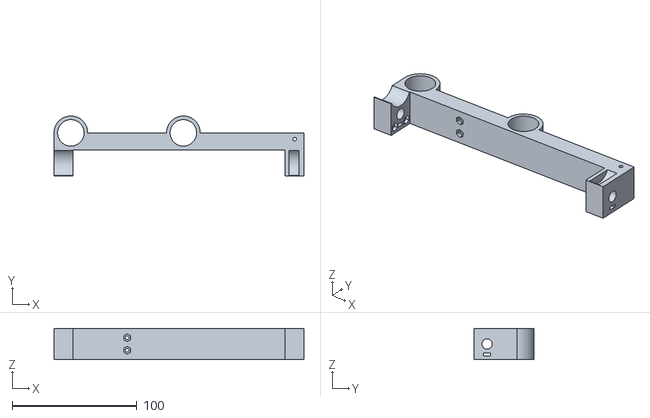
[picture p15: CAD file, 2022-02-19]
models/modelos_XYZS/freecad_base_models/slider_X_lm12uu_base_Z-full_model.stl
200.0 x 48.0 x 25.0

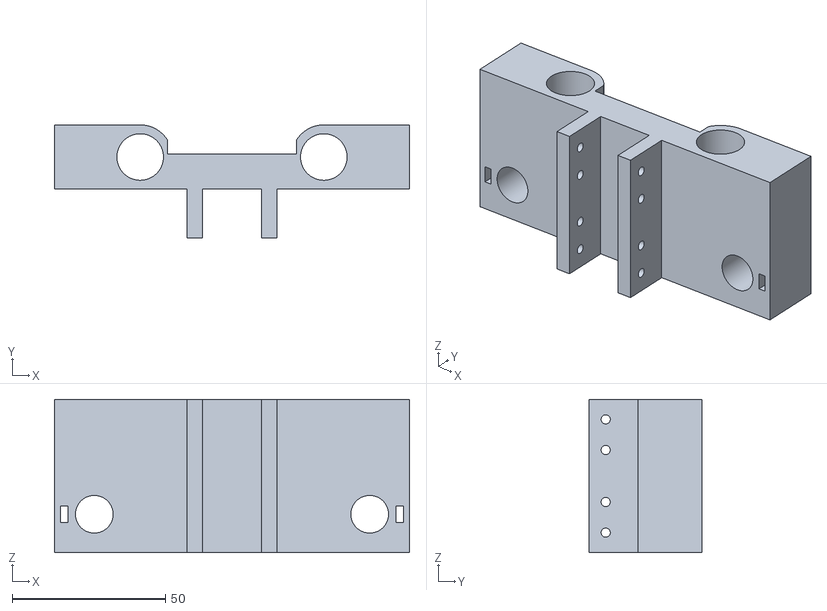
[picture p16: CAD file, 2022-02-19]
models/modelos_XYZS/freecad_base_models/base_X_lm12uu_slider_Y-full_model.stl
116.0 x 37.0 x 50.0

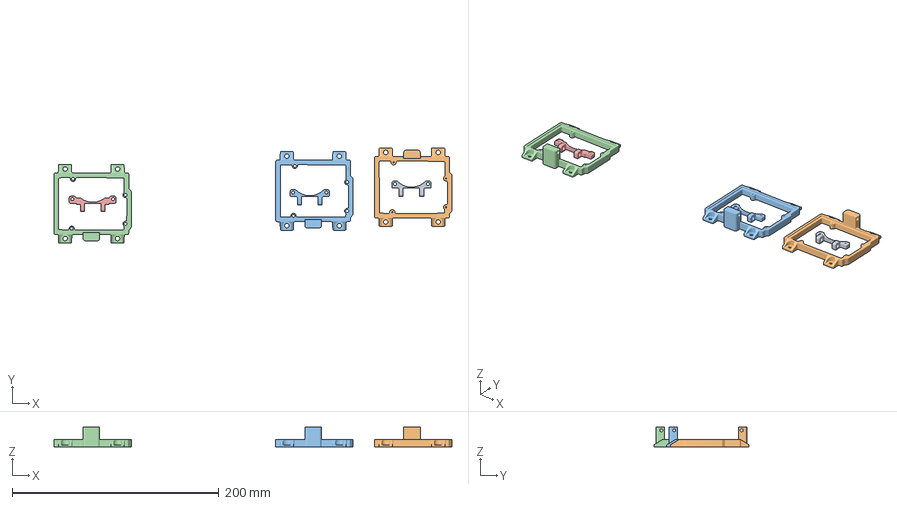
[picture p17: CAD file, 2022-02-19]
models/modelos_electronica/cooling_fan_holder/cooling_fan_holder.3mf
385.3 x 92.2 x 19.0 mm
PM_UNO_base_fan_holder.stl
PM_uno_mount_fan_mod.stl
Uno_R3_base_CNC_shield_base_with_fan_inverted.stl
base-Uno_R3_base_CNC_shield_base_with_fan_inverted.stl
clip-Uno_R3_base_CNC_shield_base_with_fan_inverted.stl

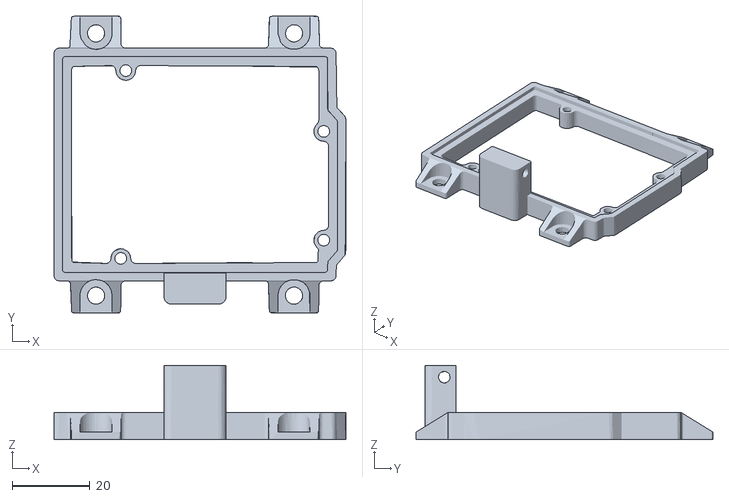
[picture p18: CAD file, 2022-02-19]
models/modelos_electronica/cooling_fan_holder/models/base-Uno_R3_base_CNC_shield_base_with_fan_inverted.stl
74.9 x 76.2 x 19.0

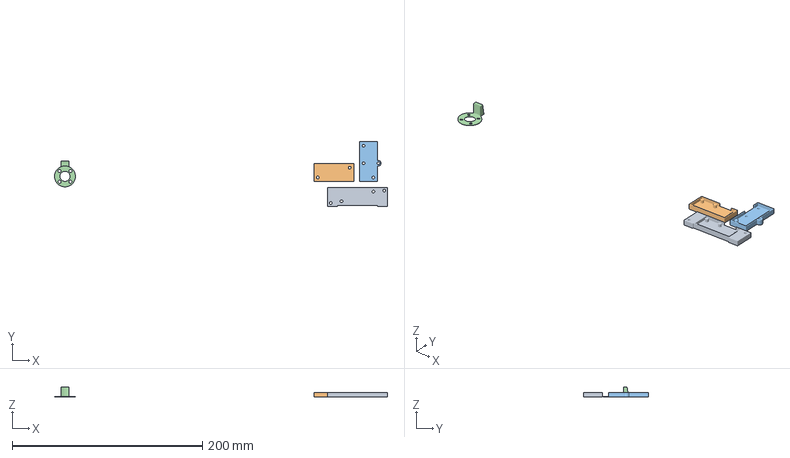
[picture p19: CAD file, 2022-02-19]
models/modelos_electronica/modelos_end_stop/end_stop_sockets.3mf
349.7 x 68.0 x 11.0 mm
tinkercad_exports.stl_1
tinkercad_exports.stl_2
tinkercad_exports.stl_3
Pippetin-grbl v0.9.5 - base para end-stops.stl

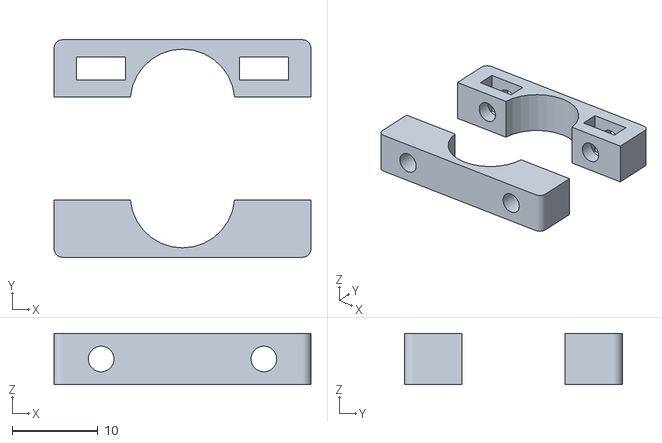
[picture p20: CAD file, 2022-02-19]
models/modelos_electronica/modelos_end_stop/freecad_base_models/end_stop_clamp_12mm.stl
30.0 x 25.4 x 6.00

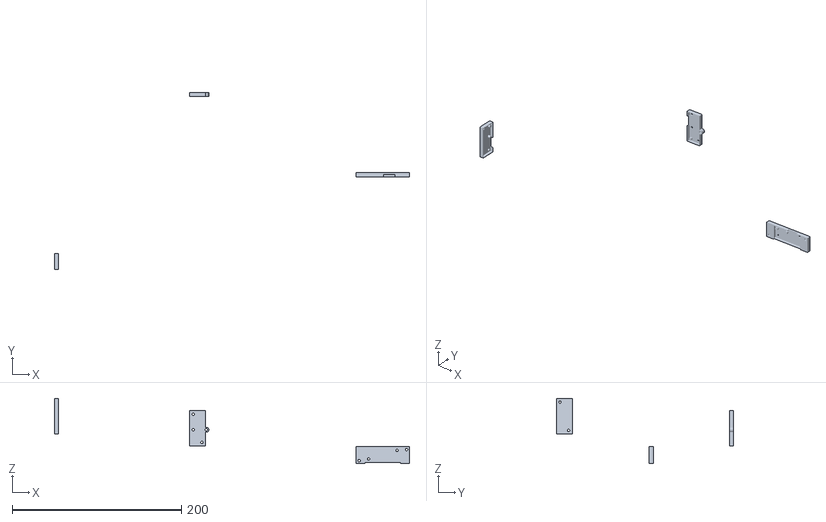
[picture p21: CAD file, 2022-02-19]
models/modelos_electronica/modelos_end_stop/tinkercad_assemblies/tinkercad_exports.stl
419.8 x 209.8 x 77.0

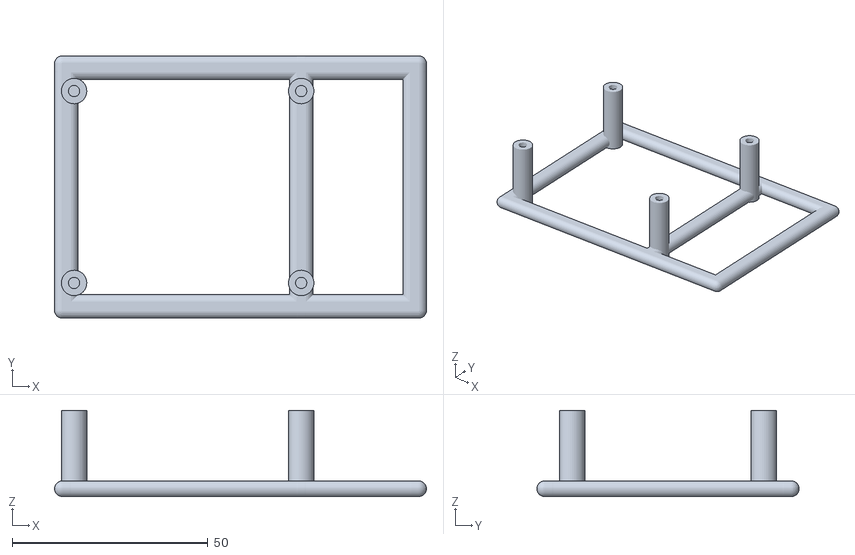
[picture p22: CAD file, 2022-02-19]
models/modelos_electronica/original_RPi_caseMulti/files/pi_front.stl
95.0 x 67.0 x 22.0

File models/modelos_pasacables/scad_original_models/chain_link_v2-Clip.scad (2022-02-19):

/*
Original Code by Joerg Scheuermann: https://www.thingiverse.com/Joerg
Original on Thingiverse: https://www.thingiverse.com/thing:8239

Clip module, Toothpick diameter Variable,
OpenSCAD/Thingiverse Customizer optimization,
Multicolor Modifier Block and extra comments
added by Gasol1n (Christian Riedl): https://www.gasol1n.com/
                                                        https://www.thingiverse.com/Gasolin

Licensed under CC BY-SA 3.0
https://creativecommons.org/licenses/by-sa/3.0/
*/

/* [Size] */
// Width of the Chain Link
width= 15;
// Length of the Chain Link
length=25;
// Height of the Chain Link
height=10;

/* [Hidden] */
// maximum allowed bending-angle
max_angle = 40; 

/* [Angles] */
// max. angle allowed to bend downwards
under_angle=-4.5; // [50]
// max. angle allowed to bend upwards
over_angle=40; // [50]

/* [Variant] */
// true - connectors go from outside to inside; false - vise versa
inner_axis=0; // [1:true, 0:false]
// true - top is closed, no holes/clip; false - top is open
closed=0; // [1:true, 0:false]
// true - a clip is used an generated instead of the toothpick hole; only works if closed=false
clip=1; // [1:true, 0:false]

/* [Further Settings] */
// Tolerance for better fit
tolerance = 0.2;
clip_extra_width = 0.5;
clip_extra_tolerance=0.05;
// Diameter of the toothpick
toothpick = 2.1; 
// Generate Modifier Block for Multicolor Stripe
multicolor_block=0; // [1:true, 0:false]
//Height of the Modifier (Multicolor) Block
mcb_height=2;

module outline(width, length, height, radius, l1, angle)
{
	y_ofs = l1 / 2;
	t = radius / 2;  // radius  = height / 2 --> t = height / 4 

	difference() {
		union() {
			translate([0, 0, height/2])    cube([width,l1,height], true);
			translate([0, -y_ofs, radius]) rotate([0, 90, 0]) cylinder(width, r = radius, center = true, $fs=0.5);
			translate([0,  y_ofs, radius]) rotate([0, 90, 0]) cylinder(width, r = radius, center = true, $fs=0.5);
			translate([0, -y_ofs, radius]) rotate([angle,     0, 0]) translate([0, -t, -t]) cube([width,radius,radius], true);
			translate([0,  y_ofs, radius]) rotate([360-angle, 0, 0]) translate([0,  t, -t]) cube([width,radius,radius], true);
            // Add material so that the base doesn't hang in the air
            translate([0,  y_ofs, radius]) rotate([360, 0, 0]) translate([0,  t, -t]) cube([width,radius,radius], true);  //  modification from original: duplicated without under angle subtraction, to make the part rest on the baseplane
            translate([0,  radius*(28*(1-cos(angle)))+y_ofs, 0]) rotate([360, 0, 0]) translate([0,  t, 0.5*radius*sin(4)]) cube([width,radius,radius*sin(4)], true);  //  modification from original: duplicated without under angle subtraction, to make the part rest on the baseplane
            // Add material so that the base doesn't hang in the air
            translate([0,  -radius*(28*(1-cos(angle)))-length/2, 0]) rotate([360, 0, 0]) translate([0,  t, 0.5*radius*sin(4)]) cube([width,radius,radius*sin(4)], true);  //  modification from original: duplicated without under angle subtraction, to make the part rest on the baseplane
            translate([0,  -length/2, 0]) rotate([360, 0, 0]) translate([0,  t, 0.5*radius*sin(4)]) cube([width,radius,radius*sin(4)], true);  //  modification from original: duplicated without under angle subtraction, to make the part rest on the baseplane
            //translate([0, 0, -(t/2)]) cube([width,length,t], true);
            }
		translate([0, 0, -(t/2)+0.005]) cube([width,length*2,t], true);  //  modification from original: +0.005 added for bug patch
	}
}

module axis(x_ofs, y_ofs, z_ofs, length, radius)
{
	rad = (radius * 0.25);
	translate([x_ofs,y_ofs,z_ofs]) rotate([0, 90, 0]) cylinder(length+tolerance, r1 = rad*1.25, r2 = rad, center = true, $fs=0.25);
}

module axis_hole(x_ofs, y_ofs, z_ofs, length, radius)
{
	rad = (radius * 0.25) * 1.25;
	translate([x_ofs,y_ofs,z_ofs]) rotate([0, 90, 0]) cylinder(length+tolerance, r1 = rad+tolerance, r2 = rad, center = true, $fs=0.25);
}

module outcut0(width, radius, h1, thick, angle, inner_axis)
{
	w = (width - thick)/2;
	t = thick + tolerance/2;

	translate([w, 0, 0]) union() {
		difference() {
			union() {
				translate([0,0,h1/2]) cube([t,radius*2, h1], true);
                translate([0,h1/2,h1/2]) cube([t,radius*2, h1], true); // modification from original: added for bug patch
				translate([0,0,h1]) rotate([angle, 0, 0]) translate([0,radius/2,0]) cube([t,radius,radius*2], true);
				translate([0,0,h1]) rotate([0, 90, 0]) cylinder(t, r = radius, center = true, $fs=0.5);
				if (inner_axis) {
					axis_hole(-(1.5*w), tolerance/2, h1,w,radius);
				}
			}
			if (!inner_axis) {
				axis(-(tolerance)/2, tolerance/2, h1,thick,radius);
			}
		}
	}
}
module outcut(width, radius, l1, h1, thick, angle, inner_axis)
{
	translate([0,l1/2,0]) union() {
		outcut0(width, radius, h1, thick, angle, inner_axis);
		mirror([1,0,0]) outcut0(width, radius, h1, thick, angle, inner_axis);
	}
}

module incut(width, radius, l1, h1, thick, angle, inner_axis)
{
	width2 = width - 2*(thick-tolerance);

	translate([0,-(l1/2),h1]) difference() {
		union() {
			translate([0,0,-(h1/2)]) cube([width2,radius*2,h1], true);
            translate([0,-h1/2,-(h1/2)]) cube([width2,radius*2,h1], true);  // modification from original: added for bug patch
			translate([0,0,0]) rotate([180-angle,0,0]) translate([0,radius/2,0]) cube([width2, radius, radius*2], true);
			translate([0,0,0]) rotate([0, 90, 0]) cylinder(width2, r = radius, center = true, $fs=0.5);
			if (!inner_axis) {
				axis_hole((width-thick)/2+tolerance, -(tolerance/2), 0,thick,radius);
				mirror([1,0,0]) axis_hole((width-thick)/2+tolerance, -(tolerance/2), 0,thick,radius);
			}
		}
		if (inner_axis) {
			axis(-((width2-thick)/2), -(tolerance/2), 0,thick,radius);
			mirror([1,0,0]) axis(-((width2-thick)/2), -(tolerance/2), 0,thick,radius);
		}
	}
}

module middle_0(length, radius, thick, closed)
{
	if (closed) {
		cube([radius*2,length,radius*2], true);
	} else {
		rotate([90, 90, 0]) cylinder(length, r = radius, center = true, $fn=50);
		translate([0,0,thick]) rotate([90, 90, 0]) cylinder(length, r = radius, center = true, $fn=50);
		translate([0,0,thick/2]) cube([2*radius,length,thick], true);
	}
}  //middle_0(10, 10, 10, false);
module middle(width, radius, length, height, l1, h1, thick, over, under, inner_axis, closed)
{
	l = length;
	th = max(thick,thick * height/width);
	h = height - (closed ?2 :1)*th;
	w = width - 4*thick;
	r = h / 2;
	scale(v=[w/h,1,1]) translate(v = [0,0,r+th]) union() {
		translate([0,h1,0]) middle_0(l, r, th, closed);
		translate([0,(l1/2)+0.1,0]) {
			difference() {
				rotate([over,0,0]) union() {
					translate([0, l/4, 0]) middle_0(l/2, r, th, closed);
					translate([0, l/4,-r]) cube([2*r,l/2,2*r], true);
				}
				translate([0, l/4,-r]) cube([2*r,l/2,2*r], true);
			}
			difference() {
				union() {  // moved thed rotate to affect only the middle_0 module
					rotate([-under,0,0]) translate([0, l/4, 0]) middle_0(l/2, r, th, closed);
					translate([0, l/4,r]) cube([2*r,l/2,2*r], true);
				}
				translate([0, l/4,r]) cube([2*r,l/2,2*r], true);
			}
		}
	}
}

module clip(width, height, length, tol=0)
{
    tol2 = tol * 2;
    cwidth = (length/10)+tol;
    cthickness = 1.5+tol;
    clength = 5;
    ccylinder = 2+tol2;
    translate([0, 0, height-(cthickness-tol2)/2])union(){
        cube([width+tol2, cwidth, cthickness], true);
        translate([width/2-(cthickness-tol2)/2, 0, -clength/2])union(){
            cube([cthickness, cwidth, clength+tol], true);
            translate([-cthickness/2, 0, -(clength/2-ccylinder/2)])rotate([90, 0, 0])cylinder(cwidth, r = ccylinder / 2, center= true, $fs=0.25);
        }
        translate([-(width/2-(cthickness-tol2)/2), 0, -clength/2])rotate([0, 0, 180])union(){
            cube([cthickness, cwidth, clength+tol], true);
            translate([-cthickness/2, 0, -(clength/2-ccylinder/2)])rotate([90, 0, 0])cylinder(cwidth, r = ccylinder / 2, center= true, $fs=0.25);
        }
    }
}

module hole(width, height, closed)
{
	if (!closed) {
		translate([0,0,height-1.5]) rotate([0, 90, 0]) cylinder(width+1, r = toothpick / 2, center = true, $fs=0.25);
	}
}

module chain_link(width, length, height, under_angle, over_angle, inner_axis, closed, clip)
{
	thick = min(2,max(1, 0.1*width));
	radius = height / 2;
	clip_len = max(length, 2*(height+thick));
	l1     = clip_len - (2 * radius);
	h1     = radius;
	under  = min(max_angle, under_angle);
	over   = min(max_angle, over_angle);
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

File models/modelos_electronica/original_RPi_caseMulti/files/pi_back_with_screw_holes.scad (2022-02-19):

//pi_back_with_screw_holes.scad by MegaSaturnv

/////////////////////////////
// Customizable Parameters //
/////////////////////////////
/* [Basic] */
//Diameter of the screw holes
SCREW_HOLE_DIAMETER = 3.5;
//Diameter of the screw head
SCREW_HEAD_DIAMETER = 5.25;

/* [Advanced] */
SCREW_HOLE_HEIGHT = 15;
SCREW_HEAD_HEIGHT = 2;
SCREW_HOLE_POS_X = 58;
SCREW_HOLE_POS_Y = 49;


/////////////
// Modules //
/////////////
module screwHole() {
	cylinder(r=SCREW_HOLE_DIAMETER/2, h=SCREW_HOLE_HEIGHT); //gap for screw thread
	cylinder(r=SCREW_HEAD_DIAMETER/2, h=SCREW_HEAD_HEIGHT); //gap for screw head
	translate([0, 0, SCREW_HEAD_HEIGHT]) cylinder(r1=SCREW_HEAD_DIAMETER/2, r2=SCREW_HOLE_DIAMETER/2, h=SCREW_HEAD_HEIGHT/2); //Cone to prevent 90 degree overhanging edges
}

module screwHole2() {
	union() {
		cylinder(r=SCREW_HOLE_DIAMETER/2, h=SCREW_HOLE_HEIGHT); //gap for screw thread
		cylinder(r=SCREW_HEAD_DIAMETER/2, h=SCREW_HEAD_HEIGHT); //gap for screw head
		translate([0, 0, SCREW_HEAD_HEIGHT]) cylinder(r1=SCREW_HEAD_DIAMETER/2, r2=SCREW_HOLE_DIAMETER/2, h=SCREW_HEAD_HEIGHT/2); //Cone to prevent 90 degree overhanging edges
	}
}


////////////////
// Main Model //
////////////////

//Use $fn = 24 if it's a preview. $fn = 96 for the render
$fn = $preview ? 24 : 96;

difference() {
	import("pi_back.stl");

	screwHole();

	translate([SCREW_HOLE_POS_X, 0, 0])
	screwHole();

	translate([0, SCREW_HOLE_POS_Y, 0])
	screwHole();

	translate([SCREW_HOLE_POS_X, SCREW_HOLE_POS_Y, 0])
	screwHole();
}

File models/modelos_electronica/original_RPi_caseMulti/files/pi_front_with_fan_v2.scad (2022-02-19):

//pi_front_with_fan_v2.scad by MegaSaturnv

/////////////////////////////
// Customizable Parameters //
/////////////////////////////
/* [Basic] */
//Diameter of the fan screw holes
FAN_SCREW_HOLE_DIAMETER = 4;
//Width of the fan screw holes mount. Should be a few mm larger than the diameter of the fan screw holes
FAN_SCREW_MOUNT_WIDTH = 8;
//Create extended screw holes for larger fans
EXTEND_SCREW_HOLES = true;
//Length of the extended screw holes
EXTEND_SCREW_HOLES_LENGTH = 26;

/* [Advanced] */

BUMPER_MIN_X = -2;
BUMPER_MIN_Y = -6;
BUMPER_MAX_X = 58;
BUMPER_MAX_Y = 55;
BUMPER_THICKNESS_Z = 4;
PEG_POS_X = 58;
PEG_POS_Y = 49;
FAN_HOLE_DIAMETER = 55;
FAN_SCREW_MOUNT_THICKNESS = BUMPER_THICKNESS_Z/2;
FAN_SCREW_MOUNT_ANGLE_ADJUSTMENT = 0;
FAN_SCREW_MOUNT_EXTENDED_ANGLE_ADJUSTMENT = 50;

/////////////
// Modules //
/////////////
module longFanScrewHole(length, width, thickness, screwWidth) {
	difference() {
		union() {
			cylinder(r=width/2, h=thickness);
			translate([0, -width/2, 0]) cube([length, width, thickness]);

			translate([length, 0, 0]) cylinder(r=width/2, h=thickness);
			//translate([length, -width/2, 0]) cube([width/2, width, thickness]);
		}
		translate([0, 0, -0.1]) cylinder(r=screwWidth/2, h=thickness+0.2);
		translate([0, -screwWidth/2, -0.1]) cube([length, screwWidth, thickness+0.2]);
		translate([length, 0, -0.1]) cylinder(r=screwWidth/2, h=thickness+0.2);
	}
}


////////////////
// Main Model //
////////////////

//Use $fn = 24 if it's a preview. $fn = 96 for the render
$fn = $preview ? 24 : 96;

union() {
	difference() {
		union() {
			import("pi_front.stl");
			translate([BUMPER_MIN_X,BUMPER_MIN_Y,0])
			cube([BUMPER_MAX_X-BUMPER_MIN_X, BUMPER_MAX_Y-BUMPER_MIN_Y, BUMPER_THICKNESS_Z]);
		}
		translate([PEG_POS_X/2, PEG_POS_Y/2, -0.1])
		cylinder(r=FAN_HOLE_DIAMETER/2, h=BUMPER_THICKNESS_Z+0.2);

		if (EXTEND_SCREW_HOLES) {
			for (i = [45, 135, 225, 315]) {
				translate([PEG_POS_X/2, PEG_POS_Y/2, -0.1]) //Translate to centre
				rotate([0, 0, i + FAN_SCREW_MOUNT_ANGLE_ADJUSTMENT]) //Rotate to each 45 degree position
				translate([FAN_HOLE_DIAMETER/2.15, 0, 0]) //Move away from centre along 45 degree angle
				rotate([0, 0, FAN_SCREW_MOUNT_EXTENDED_ANGLE_ADJUSTMENT]) //Adjust the angle at the destination
				translate([-FAN_SCREW_MOUNT_WIDTH/2, -FAN_SCREW_MOUNT_WIDTH/2, 0]) //Translate half a cube width in x and y
				cube([EXTEND_SCREW_HOLES_LENGTH + FAN_SCREW_MOUNT_WIDTH, FAN_SCREW_MOUNT_WIDTH, BUMPER_THICKNESS_Z+0.2]);
			}
		}
	}
	for (i = [45, 135, 225, 315]) {
		if (EXTEND_SCREW_HOLES) {
			difference() {
				union() {
					translate([PEG_POS_X/2, PEG_POS_Y/2, 0])
					rotate([0, 0, i + FAN_SCREW_MOUNT_ANGLE_ADJUSTMENT])
		longFanScrewHole(FAN_HOLE_DIAMETER/2.15, FAN_SCREW_MOUNT_WIDTH, FAN_SCREW_MOUNT_THICKNESS, FAN_SCREW_HOLE_DIAMETER);

					translate([PEG_POS_X/2, PEG_POS_Y/2, 0])
					rotate([0, 0, i + FAN_SCREW_MOUNT_ANGLE_ADJUSTMENT])
					translate([FAN_HOLE_DIAMETER/2.15, 0, 0])
					rotate([0, 0, FAN_SCREW_MOUNT_EXTENDED_ANGLE_ADJUSTMENT])
					longFanScrewHole(EXTEND_SCREW_HOLES_LENGTH, FAN_SCREW_MOUNT_WIDTH, FAN_SCREW_MOUNT_THICKNESS, FAN_SCREW_HOLE_DIAMETER);
				}
				translate([PEG_POS_X/2, PEG_POS_Y/2, -0.1])
				rotate([0, 0, i + FAN_SCREW_MOUNT_ANGLE_ADJUSTMENT])
				translate([FAN_HOLE_DIAMETER/2.15 - FAN_SCREW_MOUNT_WIDTH/2, -FAN_SCREW_HOLE_DIAMETER/2, 0])
				cube([FAN_SCREW_HOLE_DIAMETER*1.5, FAN_SCREW_HOLE_DIAMETER,FAN_SCREW_MOUNT_THICKNESS+0.2]);

				translate([PEG_POS_X/2, PEG_POS_Y/2, -0.1])
				rotate([0, 0, i + FAN_SCREW_MOUNT_ANGLE_ADJUSTMENT])
				translate([FAN_HOLE_DIAMETER/2.15, 0, 0])
				rotate([0, 0, FAN_SCREW_MOUNT_EXTENDED_ANGLE_ADJUSTMENT])
				translate([0, -FAN_SCREW_HOLE_DIAMETER/2, 0])
				cube([FAN_SCREW_HOLE_DIAMETER*1.5, FAN_SCREW_HOLE_DIAMETER,FAN_SCREW_MOUNT_THICKNESS+0.2]);
			}
		} else {
				translate([PEG_POS_X/2, PEG_POS_Y/2, 0])
		rotate([0, 0, i + FAN_SCREW_MOUNT_ANGLE_ADJUSTMENT])
		longFanScrewHole(FAN_HOLE_DIAMETER/2.15, FAN_SCREW_MOUNT_WIDTH, FAN_SCREW_MOUNT_THICKNESS, FAN_SCREW_HOLE_DIAMETER);
		}
	}
}

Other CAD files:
models/modelos_pasacables/freecad_port_models/models_freecad/cable_carrier_fc_assembly.stl
models/modelos_electronica/original_RPi_caseMulti/picasemulti.3mf
models/modelos_electronica/PCB_base/PCB base - Simple.3mf
models/modelos_electronica/PCB_base/tinkercad_export/PCB base - Simple with fan mount.stl
models/modelos_XYZS/modelos_poleas_GT2/parametric_pulley/Pulley_T-MXL-XL-HTD-GT2_N-tooth.scad
models/M3_screw_and_nut.stl
models/modelos_XYZS/Pippetin-grbl v0.99 - freecad_base_models.3mf
models/modelos_XYZS/Pippetin-grbl v0.99 - freecad_pipetting_models.3mf
models/modelos_XYZS/Pippetin-grbl v0.99 - tinkercad_export_models.3mf
models/modelos_XYZS/freecad_base_models/X_stepper_coupling.stl
models/modelos_XYZS/freecad_base_models/base_stepper_correa.stl
models/modelos_XYZS/freecad_base_models/base_stepper_correa_screw_pocket.stl
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

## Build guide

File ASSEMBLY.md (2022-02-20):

2) Guia de Construccion
 - Guia completa para armar el hardware

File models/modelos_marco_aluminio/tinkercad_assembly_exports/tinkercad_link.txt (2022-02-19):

https://www.tinkercad.com/things/gpudXXik4lF-terrific-bigery-esboo/edit

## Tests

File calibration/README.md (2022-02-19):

# Pipette callibration

Herein lie the micropipette callibration notes.

Standard micropipettes are meant to be used by hand,
but we use a stepper, which needed corrections to
gather and dispense the correct solution volumes.

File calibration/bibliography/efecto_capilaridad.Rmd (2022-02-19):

---
title: "Effect of capillary pressure"
---

## Efecto de la capilaridad

En `bibliography/Technical_note_Pipettes_1118.pdf` (pg. 4) aparece la siguiente ecuación:

$$
\Delta V \sim -V_D \cdot \frac{\Delta p_s}{p_a}
$$

Relaciona el efecto de la capilaridad sobre el volumen, donde:

* $V_D$ es el _captive air volume_.
* $p_a$ es la presión barométrica.
* $p_s$ es la presión "capilar".

Tal que:

$$
p_s = \frac{4 \cdot \sigma \cdot cos(\theta)}{d}
$$

Donde:

* $\sigma$ es la tensión superficial.
* $d$ es el diámetro interno del tip.
* $\theta$ es el ángulo de contacto entre el líquido y el tip.

De estas cosas, intuyo que una de las más influyentes es $d$.
En cambio, no veo por qué $\theta$ cambiaría demasiado en la interfaz con el aire.
Y $\sigma$ es constante para una solución fija, así que no molesta si uso solo agua.

Debe ser difícil corregir esto, por eso las pipetas tienen un límite inferior, y después hay que cambiar de pipeta/tip.

## p200 tips

En internet hay una foto de Millenial que dice 0.53 mm (D.I.).

Unas de corning dicen 0.028'' (D.I.) o sea 0.71 mm (D.I.).

Ver: https://certs-ecatalog.corning.com/life-sciences/product-descriptions/4711.pdf

## función de corrección

La pregunta es como depende $d$ de la cantidad de volumen restante en el tip, y si puedo hacer alguna corrección para el dispensing a bajo volumen.

En ese caso la forma funcional sería la siguiente $\Delta V \ \propto \frac{1}{d_{final}} - \frac{1}{d_{inicial}}$.

Poniendo algun dato:

$$
\Delta V_{p_s} \ \propto \frac{1}{0.6 mm} - \frac{1}{d_{inicial}}
$$

Donde $d_{inicial}$ depende de cuanto volumen queda en el tip (a que altura del cono del tip está el líquido).

Si grafico:

```{r}
f <- function(x) (1/6) - (1/x)
curve(expr = f,
      from = 2/6, # 0.333
      to = 1/6)   # 0.166
```

Ahora, si quito la ordenada, la forma es igual.

La idea es que mientras más grande sea la diferencia en volumen (eje x creciente),
mayor es la diferencia de presión, pero ese efecto se achata a la larga, 
y por eso es despreciable.

En este plot se ve eso más marcadamente, graficando hacia X mayores:

```{r}
f <- function(x) -1/x
curve(expr = f,
      from = 1/6, # 0.333
      to = 1)   # 0.166
```

Aunque eso es más correcto, quizás no sea del todo necesario, y pueda safar con una recta a volumenes bajos.

La función que me serviría es una que "agrega" volumen dispensado.

Mi error con s_retract=5 es de -2 uL, así que al final debería tener un volumen extra de 2.

A grandes rasgos:

> Si el volumen final es menor a 20 uL:
> 
> Aplicar una corrección lineal donde se agrega 1 uL por cada 10 uL pipeteados.

Alternativamente:

> Si el volumen final es menor a 20 uL:
> 
> Aplicar una corrección recíproca donde se agrega 1 uL por cada 10 uL pipeteados (de forma no lineal: 1/x).

Esta curva hace eso, por cada uL que se pasa del límite de 20 uL, agrega un poco, hasta llegar a 2 uL cuando ya no queda nada en el tip.

```{r}
f <- function(x) abs((-1/(15+1-x) + 0.04761905) * (2/0.952381))
f <- function(x, start_vol=20, max_cor=2) -abs(-x*max_cor/start_vol+max_cor)
curve(expr = f,
      from = 0, # 0.333
      to = 20)   # 0.166

f(3)
```

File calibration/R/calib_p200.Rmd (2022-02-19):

---
title: "Calibracion p200"
output:
  html_document:
    df_print: paged
    toc: yes
    toc_float: true
    toc_depth: 2
    number_sections: false
    smooth_scroll: false
    code_folding: hide
  pdf_document:
    latex_engine: xelatex
    toc: true
    toc_depth: 2
    number_sections: true
editor_options:
  chunk_output_type: inline
author: NM
date: "9 abril, 2021"
urlcolor: blue
---

<!-- setup chunk -->

```{r setup, message=F}
knitr::opts_chunk$set(message = F)
knitr::opts_knit$set(root.dir = here::here())
# library(utiles)

# knitr::opts_chunk$set(cache = T)
library(dplyr)
# library(tidyr)
# library(purrr)
# library(plotly)
library(ggplot2)
# library(renv)
```

<!-- your code -->

## Load data

```{r}
datos <- read.csv("data/calib_p200.csv")

datos
```

## Have fun!

```{r}
datos <- datos %>% mutate(delta_masa = peso_final - peso_inicial,
                          gui_vol = Vol) %>% 
  select(-nota, -Vol)

datos
```

```{r}
ggplot(datos, aes(x=gui_vol, delta_masa)) +
  geom_point(alpha=.5) +
  geom_abline(slope = 1/1000, intercept = 0) +
  coord_cartesian(ylim = c(0, 0.12), xlim=c(0,120))

# ggsave("results/calib_p200.png")

ggplot(datos, aes(x=as.factor(gui_vol), 1000*delta_masa-gui_vol, color=as.factor(gui_vol))) +
  geom_jitter(width = 0.1) +
  ylab("Diferencia") +
  xlab("Volumen esperado") +
  ggtitle("Diferencia del volumen pipeteado respecto al esperado") +
  theme_minimal()

# ggsave("results/calib_p200.diff.png")
```

```{r}
sample.n <- 3
alpha = 0.05
degrees.freedom = sample.n - 1
t.score = qt(p=alpha/2, df=degrees.freedom,lower.tail=F)

datos %>% 
  mutate(real_vol = delta_masa * 1000) %>% 
  group_by(gui_vol) %>% 
  summarise(real_vol.mean = mean(real_vol), real_vol.sd = sd(real_vol),
            real_vol.se = sd(real_vol)/sqrt(n())) %>% 
  mutate(ci = t.score * real_vol.se) %>% 
  mutate(rel.ci.error = 100*ci/real_vol.mean,
         rel.sd.error = 100*real_vol.sd*2/real_vol.mean)
```

El error aleatorio esta cerca de +/- 0.75% para los target volumes 70 y 120. Pero para 30 es +/- 6.7% (hay dos puntos cerca y uno lejos, pero no parece un outlier).

Nota: use $2\sigma$ como criterio de error (~90% de chance de ver un dato en el intervalo $\mu \pm 2 \sigma$).

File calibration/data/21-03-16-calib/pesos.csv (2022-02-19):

tubo | peso_inicial | peso_final | vol | orden_en_secuencia
1 | 1.1093 | 1.1342 | 2 | 1
2 | 1.1088 | 1.1350 | 2 | 2
3 | 1.1070 | 1.1328 | 2 | 3
4 | 1.1088 | 1.1338 | 2 | 4
5 | 1.1587 | 1.1846 | 2 | 5
1 | 1.1093 | 1.1089 | -2 | 1
2 | 1.1088 | 1.1101 | -2 | 2
3 | 1.1070 | 1.1076 | -2 | 3
4 | 1.1088 | 1.1083 | -2 | 4
5 | 1.1587 | 1.1615 | -2 | 5

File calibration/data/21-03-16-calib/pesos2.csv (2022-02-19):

tubo | peso_inicial | peso_final | vol | orden_en_secuencia
1 | 1.1093 | 1.1342 | 2 | 1
2 | 1.1088 | 1.1350 | 2 | 2
3 | 1.1070 | 1.1328 | 2 | 3
4 | 1.1088 | 1.1338 | 2 | 4
5 | 1.1587 | 1.1846 | 2 | 5
1 | 1.1342 | 1.1089 | -2 | 1
2 | 1.1350 | 1.1101 | -2 | 2
3 | 1.1328 | 1.1076 | -2 | 3
4 | 1.1338 | 1.1083 | -2 | 4
5 | 1.1846 | 1.1615 | -2 | 5

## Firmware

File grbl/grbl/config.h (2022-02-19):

/*
  config.h - compile time configuration
  Part of Grbl

  Copyright (c) 2012-2016 Sungeun K. Jeon for Gnea Research LLC
  Copyright (c) 2009-2011 Simen Svale Skogsrud

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
  You should have received a copy of the GNU General Public License
  along with Grbl.  If not, see <http://www.gnu.org/licenses/>.
*/

// This file contains compile-time configurations for Grbl's internal system. For the most part,
// users will not need to directly modify these, but they are here for specific needs, i.e.
// performance tuning or adjusting to non-typical machines.

// IMPORTANT: Any changes here requires a full re-compiling of the source code to propagate them.

#ifndef config_h
#define config_h
#include "grbl.h" // For Arduino IDE compatibility.


// Define CPU pin map and default settings.
// NOTE: OEMs can avoid the need to maintain/update the defaults.h and cpu_map.h files and use only
// one configuration file by placing their specific defaults and pin map at the bottom of this file.
// If doing so, simply comment out these two defines and see instructions below.
#define DEFAULTS_GENERIC
#define CPU_MAP_ATMEGA328P // Arduino Uno CPU

// Serial baud rate
// #define BAUD_RATE 230400
#define BAUD_RATE 115200

// Define realtime command special characters. These characters are 'picked-off' directly from the
// serial read data stream and are not passed to the grbl line execution parser. Select characters
// that do not and must not exist in the streamed g-code program. ASCII control characters may be
// used, if they are available per user setup. Also, extended ASCII codes (>127), which are never in
// g-code programs, maybe selected for interface programs.
// NOTE: If changed, manually update help message in report.c.

#define CMD_RESET 0x18 // ctrl-x.
#define CMD_STATUS_REPORT '?'
#define CMD_CYCLE_START '~'
#define CMD_FEED_HOLD '!'

// NOTE: All override realtime commands must be in the extended ASCII character set, starting
// at character value 128 (0x80) and up to 255 (0xFF). If the normal set of realtime commands,
// such as status reports, feed hold, reset, and cycle start, are moved to the extended set
// space, serial.c's RX ISR will need to be modified to accomodate the change.
// #define CMD_RESET 0x80
// #define CMD_STATUS_REPORT 0x81
// #define CMD_CYCLE_START 0x82
// #define CMD_FEED_HOLD 0x83
#define CMD_SAFETY_DOOR 0x84
#define CMD_JOG_CANCEL  0x85
#define CMD_DEBUG_REPORT 0x86 // Only when DEBUG enabled, sends debug report in '{}' braces.
#define CMD_FEED_OVR_RESET 0x90         // Restores feed override value to 100%.
#define CMD_FEED_OVR_COARSE_PLUS 0x91
#define CMD_FEED_OVR_COARSE_MINUS 0x92
#define CMD_FEED_OVR_FINE_PLUS  0x93
#define CMD_FEED_OVR_FINE_MINUS  0x94
#define CMD_RAPID_OVR_RESET 0x95        // Restores rapid override value to 100%.
#define CMD_RAPID_OVR_MEDIUM 0x96
#define CMD_RAPID_OVR_LOW 0x97
// #define CMD_RAPID_OVR_EXTRA_LOW 0x98 // *NOT SUPPORTED*
#define CMD_SPINDLE_OVR_RESET 0x99      // Restores spindle override value to 100%.
#define CMD_SPINDLE_OVR_COARSE_PLUS 0x9A
#define CMD_SPINDLE_OVR_COARSE_MINUS 0x9B
#define CMD_SPINDLE_OVR_FINE_PLUS 0x9C
#define CMD_SPINDLE_OVR_FINE_MINUS 0x9D
#define CMD_SPINDLE_OVR_STOP 0x9E
#define CMD_COOLANT_FLOOD_OVR_TOGGLE 0xA0
#define CMD_COOLANT_MIST_OVR_TOGGLE 0xA1

// If homing is enabled, homing init lock sets Grbl into an alarm state upon power up. This forces
// the user to perform the homing cycle (or override the locks) before doing anything else. This is
// mainly a safety feature to remind the user to home, since position is unknown to Grbl.
#define HOMING_INIT_LOCK // Comment to disable

// Define the homing cycle patterns with bitmasks. The homing cycle first performs a search mode
// to quickly engage the limit switches, followed by a slower locate mode, and finished by a short
// pull-off motion to disengage the limit switches. The following HOMING_CYCLE_x defines are executed
// in order starting with suffix 0 and completes the homing routine for the specified-axes only. If
// an axis is omitted from the defines, it will not home, nor will the system update its position.
// Meaning that this allows for users with non-standard cartesian machines, such as a lathe (x then z,
// with no y), to configure the homing cycle behavior to their needs.
// NOTE: The homing cycle is designed to allow sharing of limit pins, if the axes are not in the same
// cycle, but this requires some pin settings changes in cpu_map.h file. For example, the default homing
// cycle can share the Z limit pin with either X or Y limit pins, since they are on different cycles.
// By sharing a pin, this frees up a precious IO pin for other purposes. In theory, all axes limit pins
// may be reduced to one pin, if all axes are homed with seperate cycles, or vice versa, all three axes
// on separate pin, but homed in one cycle. Also, it should be noted that the function of hard limits
// will not be affected by pin sharing.
// NOTE: Defaults are set for a traditional 3-axis CNC machine. Z-axis first to clear, followed by X & Y.
#define HOMING_CYCLE_0 (1<<Z_AXIS)                // REQUIRED: First move Z to clear workspace.
#define HOMING_CYCLE_1 ((1<<X_AXIS)|(1<<Y_AXIS))  // OPTIONAL: Then move X,Y at the same time.
// #define HOMING_CYCLE_2                         // OPTIONAL: Uncomment and add axes mask to enable

// NOTE: The following are two examples to setup homing for 2-axis machines.
// #define HOMING_CYCLE_0 ((1<<X_AXIS)|(1<<Y_AXIS))  // NOT COMPATIBLE WITH COREXY: Homes both X-Y in one cycle. 

// #define HOMING_CYCLE_0 (1<<X_AXIS)  // COREXY COMPATIBLE: First home X
// #define HOMING_CYCLE_1 (1<<Y_AXIS)  // COREXY COMPATIBLE: Then home Y

// Number of homing cycles performed after when the machine initially jogs to limit switches.
// This help in preventing overshoot and should improve repeatability. This value should be one or
// greater.
#define N_HOMING_LOCATE_CYCLE 1 // Integer (1-128)

// Enables single axis homing commands. $HX, $HY, and $HZ for X, Y, and Z-axis homing. The full homing 
// cycle is still invoked by the $H command. This is disabled by default. It's here only to address
// users that need to switch between a two-axis and three-axis machine. This is actually very rare.
// If you have a two-axis machine, DON'T USE THIS. Instead, just alter the homing cycle for two-axes.
// #define HOMING_SINGLE_AXIS_COMMANDS // Default disabled. Uncomment to enable.

// After homing, Grbl will set by default the entire machine space into negative space, as is typical
// for professional CNC machines, regardless of where the limit switches are located. Uncomment this
// define to force Grbl to always set the machine origin at the homed location despite switch orientation.
// #define HOMING_FORCE_SET_ORIGIN // Uncomment to enable.

// Number of blocks Grbl executes upon startup. These blocks are stored in EEPROM, where the size
// and addresses are defined in settings.h. With the current settings, up to 2 startup blocks may
// be stored and executed in order. These startup blocks would typically be used to set the g-code
// parser state depending on user preferences.
#define N_STARTUP_LINE 2 // Integer (1-2)

// Number of floating decimal points printed by Grbl for certain value types. These settings are
// determined by realistic and commonly observed values in CNC machines. For example, position
// values cannot be less than 0.001mm or 0.0001in, because machines can not be physically more
// precise this. So, there is likely no need to change these, but you can if you need to here.
// NOTE: Must be an integer value from 0 to ~4. More than 4 may exhibit round-off errors.
#define N_DECIMAL_COORDVALUE_INCH 4 // Coordinate or position value in inches
#define N_DECIMAL_COORDVALUE_MM   3 // Coordinate or position value in mm
#define N_DECIMAL_RATEVALUE_INCH  1 // Rate or velocity value in in/min
#define N_DECIMAL_RATEVALUE_MM    0 // Rate or velocity value in mm/min
#define N_DECIMAL_SETTINGVALUE    3 // Decimals for floating point setting values
#define N_DECIMAL_RPMVALUE        0 // RPM value in rotations per min.

// If your machine has two limits switches wired in parallel to one axis, you will need to enable
// this feature. Since the two switches are sharing a single pin, there is no way for Grbl to tell
// which one is enabled. This option only effects homing, where if a limit is engaged, Grbl will
// alarm out and force the user to manually disengage the limit switch. Otherwise, if you have one
// limit switch for each axis, don't enable this option. By keeping it disabled, you can perform a
// homing cycle while on the limit switch and not have to move the machine off of it.
// #define LIMITS_TWO_SWITCHES_ON_AXES

// Allows GRBL to track and report gcode line numbers.  Enabling this means that the planning buffer
// goes from 16 to 15 to make room for the additional line number data in the plan_block_t struct
// #define USE_LINE_NUMBERS // Disabled by default. Uncomment to enable.

// Upon a successful probe cycle, this option provides immediately feedback of the probe coordinates
// through an automatically generated message. If disabled, users can still access the last probe
// coordinates through Grbl '$#' print parameters.
#define MESSAGE_PROBE_COORDINATES // Enabled by default. Comment to disable.

// Enables a second coolant control pin via the mist coolant g-code command M7 on the Arduino Uno
// analog pin 4. Only use this option if you require a second coolant control pin.
// NOTE: The M8 flood coolant control pin on analog pin 3 will still be functional regardless.
// #define ENABLE_M7 // Disabled by default. Uncomment to enable.

// This option causes the feed hold input to act as a safety door switch. A safety door, when triggered,
// immediately forces a feed hold and then safely de-energizes the machine. Resuming is blocked until
// the safety door is re-engaged. When it is, Grbl will re-energize the machine and then resume on the
// previous tool path, as if nothing happened.
// #define ENABLE_SAFETY_DOOR_INPUT_PIN // Default disabled. Uncomment to enable.

// After the safety door switch has been toggled and restored, this setting sets the power-up delay
// between restoring the spindle and coolant and resuming the cycle.
#define SAFETY_DOOR_SPINDLE_DELAY 4.0 // Float (seconds)
#define SAFETY_DOOR_COOLANT_DELAY 1.0 // Float (seconds)

// Enable CoreXY kinematics. Use ONLY with CoreXY machines.
// IMPORTANT: If homing is enabled, you must reconfigure the homing cycle #defines above to
// #define HOMING_CYCLE_0 (1<<X_AXIS) and #define HOMING_CYCLE_1 (1<<Y_AXIS)
// NOTE: This configuration option alters the motion of the X and Y axes to principle of operation
// defined at (http://corexy.com/theory.html). Motors are assumed to positioned and wired exactly as
// described, if not, motions may move in strange directions. Grbl requires the CoreXY A and B motors
// have the same steps per mm internally.
// #define COREXY // Default disabled. Uncomment to enable.

// Inverts pin logic of the control command pins based on a mask. This essentially means you can use
// normally-closed switches on the specified pins, rather than the default normally-open switches.
// NOTE: The top option will mask and invert all control pins. The bottom option is an example of
// inverting only two control pins, the safety door and reset. See cpu_map.h for other bit definitions.
// #define INVERT_CONTROL_PIN_MASK CONTROL_MASK // Default disabled. Uncomment to disable.
// #define INVERT_CONTROL_PIN_MASK ((1<<CONTROL_SAFETY_DOOR_BIT)|(1<<CONTROL_RESET_BIT)) // Default disabled.
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

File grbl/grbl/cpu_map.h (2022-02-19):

/*
  cpu_map.h - CPU and pin mapping configuration file
  Part of Grbl

  Copyright (c) 2012-2016 Sungeun K. Jeon for Gnea Research LLC

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
  You should have received a copy of the GNU General Public License
  along with Grbl.  If not, see <http://www.gnu.org/licenses/>.
*/

/* The cpu_map.h files serve as a central pin mapping selection file for different
   processor types or alternative pin layouts. This version of Grbl officially supports
   only the Arduino Mega328p. */


#ifndef cpu_map_h
#define cpu_map_h


#ifdef CPU_MAP_ATMEGA328P // (Arduino Uno) Officially supported by Grbl.

  // Define serial port pins and interrupt vectors.
  #define SERIAL_RX     USART_RX_vect
  #define SERIAL_UDRE   USART_UDRE_vect

  // Define step pulse output pins. NOTE: All step bit pins must be on the same port.
  #define STEP_DDR        DDRD
  #define STEP_PORT       PORTD
  #define X_STEP_BIT      2  // Uno Digital Pin 2
  #define Y_STEP_BIT      3  // Uno Digital Pin 3
  #define Z_STEP_BIT      4  // Uno Digital Pin 4
  #define STEP_MASK       ((1<<X_STEP_BIT)|(1<<Y_STEP_BIT)|(1<<Z_STEP_BIT)) // All step bits

  // Define step direction output pins. NOTE: All direction pins must be on the same port.
  #define DIRECTION_DDR     DDRD
  #define DIRECTION_PORT    PORTD
  #define X_DIRECTION_BIT   5  // Uno Digital Pin 5
  #define Y_DIRECTION_BIT   6  // Uno Digital Pin 6
  #define Z_DIRECTION_BIT   7  // Uno Digital Pin 7
  #define DIRECTION_MASK    ((1<<X_DIRECTION_BIT)|(1<<Y_DIRECTION_BIT)|(1<<Z_DIRECTION_BIT)) // All direction bits

  // Define stepper driver enable/disable output pin.
  #define STEPPERS_DISABLE_DDR    DDRB
  #define STEPPERS_DISABLE_PORT   PORTB
  #define STEPPERS_DISABLE_BIT    0  // Uno Digital Pin 8
  #define STEPPERS_DISABLE_MASK   (1<<STEPPERS_DISABLE_BIT)

  // Define homing/hard limit switch input pins and limit interrupt vectors.
  // NOTE: All limit bit pins must be on the same port, but not on a port with other input pins (CONTROL).
  #define LIMIT_DDR        DDRB
  #define LIMIT_PIN        PINB
  #define LIMIT_PORT       PORTB
  #define X_LIMIT_BIT      1  // Uno Digital Pin 9
  #define Y_LIMIT_BIT      2  // Uno Digital Pin 10
  #ifdef VARIABLE_SPINDLE // Z Limit pin and spindle enabled swapped to access hardware PWM on Pin 11.
    #define Z_LIMIT_BIT	   4 // Uno Digital Pin 12
  #else
    #define Z_LIMIT_BIT    3  // Uno Digital Pin 11
  #endif
  #if !defined(ENABLE_DUAL_AXIS)
    #define LIMIT_MASK     ((1<<X_LIMIT_BIT)|(1<<Y_LIMIT_BIT)|(1<<Z_LIMIT_BIT)) // All limit bits
  #endif
  #define LIMIT_INT        PCIE0  // Pin change interrupt enable pin
  #define LIMIT_INT_vect   PCINT0_vect
  #define LIMIT_PCMSK      PCMSK0 // Pin change interrupt register
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

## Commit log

2022-02-19 Import latest commit from dev (0fb9517)
    [21-06-15-p200-calib_1.csv, 21-06-15-p200-calib_2.csv, calib_p200-21_06_01.csv, calib_p200-21_06_02-segunda.csv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]
2022-02-19 Added remaining files to repo
    [2020.FCStd, 2020_slider_nut.stl, 2020_slider_nut_tol02.stl, 2020_slider_only_tol02.stl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]

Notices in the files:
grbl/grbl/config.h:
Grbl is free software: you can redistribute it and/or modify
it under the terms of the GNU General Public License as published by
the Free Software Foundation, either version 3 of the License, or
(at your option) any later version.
